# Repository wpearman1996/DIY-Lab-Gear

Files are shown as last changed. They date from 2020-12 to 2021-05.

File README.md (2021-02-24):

# DIY-Lab-Gear
3D Print and DIY designed lab equipment
**Vacuum manifold**
To assemble this, you need:
1) 14 M3 20mm hex head (ideally) screws
2) 13 5.5M M3 square nuts
3) A sheet of neoprene or equivalent rubber - I just went to a local rubber store and bought a few sheets and tried out a range.

To assemble, place the thin piece of printed plastic over the neoprene and cut around it to create the rubber layer that will act as the seal. This piece of plastic is just a stencil to get the size right - adjust to make sure it fits with your plates.

Use the top piece of plastic with the screw holes in it and place it over the neoprene and use a drill to make holes in the right spaces on the neoprene.

Align this piece with the neoprene and push the screws through the holes in the top piece of plastic and the neoprene.

Using a soldering iron, gently heat up the square nuts and push them into the holes in the side of the main piece, this will act as a thread to help the screws screw in it. Make sure the thread aligns with the screw hole.

Align the neoprene and plastic piece, and gently screw everything together. If you want, apply a layer of silicone on the outside to help make it airtight. 

I printed this with 15% infill, PLA, 0.3mm layer height, and with 20mm brim. I customized supports to have supports only on the vacuum pump attachment - so no supports were in the slots for the nuts. 

Do not use anything particularly reactive or toxic with this, unless you seal it fully with epoxy resin for similar - as you risk damaging the manifold. After use, rinse with sterile water into a waste container. Currently we have this set up to feed into a waste flask to which the vacuum pump is applied to - so that the liquid waste (and water after rinsing) is easily collected. Do not autoclave, or heat up to dry - just pat dry then leave to fully air dry. 

Future iterations will have a slot for a glass tank to collect the liquid waste so it doesn't come in direct contact with the manifold.

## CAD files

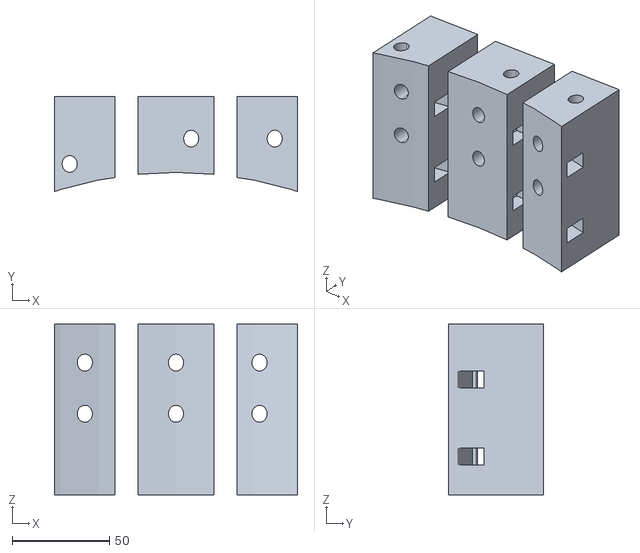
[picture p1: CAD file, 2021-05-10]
Amazing Habbi-Jarv(1).stl
125.0 x 49.0 x 87.7

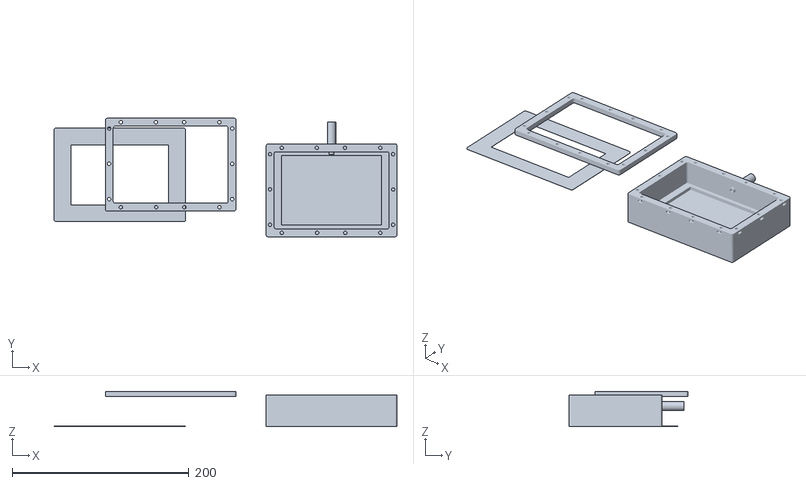
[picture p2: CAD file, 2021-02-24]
vacuum manifold.stl
388.0 x 134.2 x 40.0

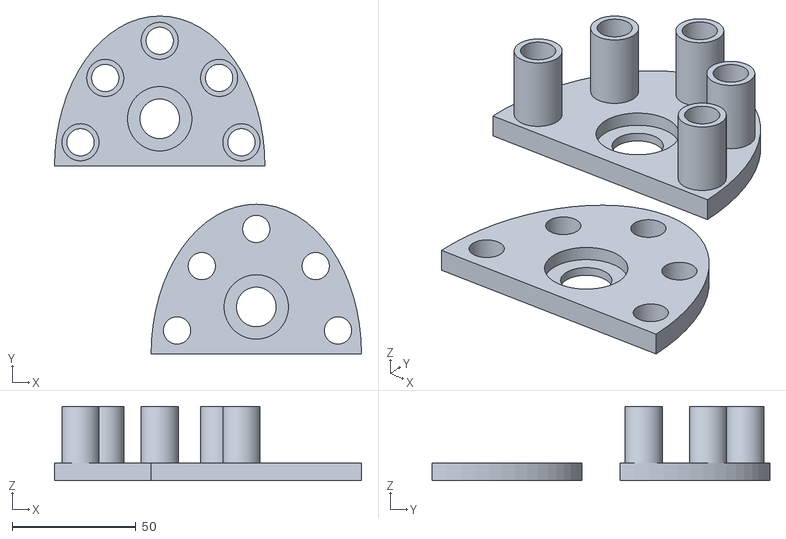
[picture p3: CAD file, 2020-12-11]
bead_beater_attachment_multitool.stl
124.0 x 136.5 x 30.0

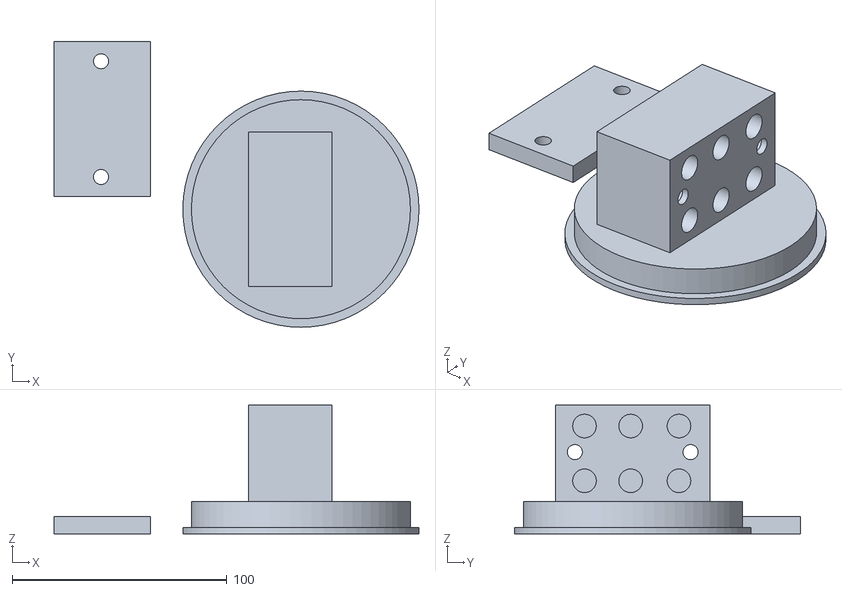
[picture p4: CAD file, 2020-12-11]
bead_beater_pipe_fitting.stl
170.0 x 133.0 x 60.0
